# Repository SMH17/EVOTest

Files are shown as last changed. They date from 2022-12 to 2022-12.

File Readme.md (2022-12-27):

Test olive oil quality using a laser diode with wavelength in 405nm-445nm range to check absorbance properties of chlorophyll and elicit its fluorescence and a TCS34725 sensor to analyze color spectrum, considering that chlorophyll fluorescence emission peaks around 680nm-700nm wavelength and chlorophyl absorbance peaks around 400nm-450nm wavelength.
In EVO oils the chlorophyll isn't destroyed by chemical processing and heat treatments, so it gives a clue of oil quality.
It is also important to note that this test cannot directly measure the oil acidity, however if the oil has high acidity level the chlorophyll will degrade faster over the time. 

NOTES:
- The project model and firmware code are just preliminary concept versions that could be improved refining the current analysis method and adding additional modules and test routines to evaluate other aspects.
- This code has been optimized for the use with STM32F030F4P6 and has been tested on STM32F030F4 Demo Board, in order to fit in small flash of this board the default Arduino USART serial support must be disabled.
- This code uses customized libraries so they aren’t available in standard repositories. Use the libraries provided e.g., copying them from libs folder to your Arduino\libraries folder (or configuring them properly for whatever IDE you use).
- Use low power <5mW laser diodes (as the one used for pointers), do not use high power lasers.
- Laser modules even at same wavelength and power level may have different lens configuration and collimation, so you need to do some calibration to get consistent results with different laser modules. 
- The stereolithographic files STL in 3D models libraries can be easily printed with common FDM 3D printer and filaments, however make sure to avoid to use transparent materials that could make filter external light in analysis chamber, this is very important. (I have used black PLA to print my prototype.)

Check [PDF documentation](https://github.com/SMH17/EVOTest/blob/main/EVOTest.pdf) for more details.

Version: 0.1a

Website:
www.silviomarano.tk

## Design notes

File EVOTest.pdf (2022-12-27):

EVOTest by Silvio Marano – v0.1a – 2020

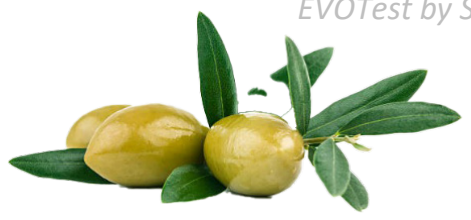
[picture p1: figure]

# EVOTest

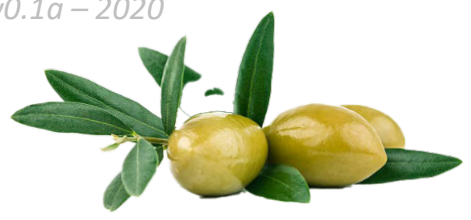
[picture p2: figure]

Olive oil is very appreciated however its quality varies a lot and often is distributed as EVO (extra virgin olive oil) subpar oil that isn’t really eligible for that label.
EVOTest is an open-source electronic project that allows to easily test olive oil quality.

## WORKING PRINCIPLE

An olive oil to be label EVO must be extracted without chemical processing and at temperatures lower than 33°C or lower than 27°C (cold extraction) for the higher quality ones, and an acidity level not higher than 0.8°.
These conditions grant that oil contains chlorophyll that isn't degraded by chemical processing, high temperature heat treatments (all methods used to increase oil extraction quantity at detriment of its characteristics), so its presence gives a clue of oil quality. Chlorophyll has also interesting properties that can be used to evaluate its presence and\or integrity.
EVOTest uses a laser diode with wavelength in 405nm-445nm range to check absorbance properties of chlorophyll and elicit its fluorescence and a sensor to analyze color spectrum, considering that chlorophyll fluorescence emission peaks around 680nm-700nm (red light spectrum) wavelength and chlorophyl absorbance peaks around 400nm-450nm wavelength.

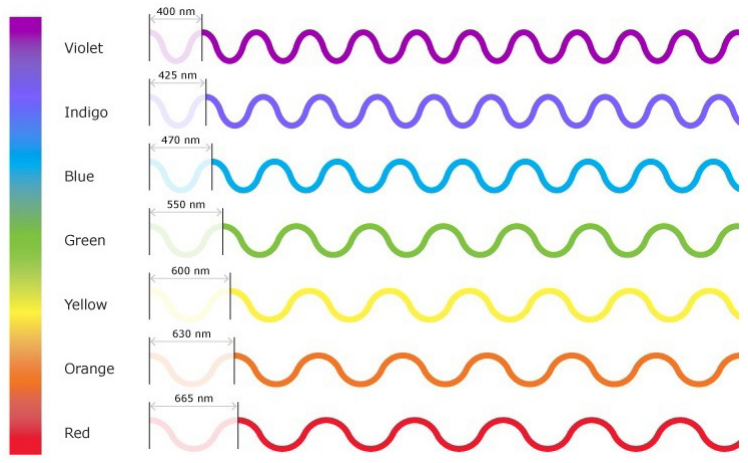
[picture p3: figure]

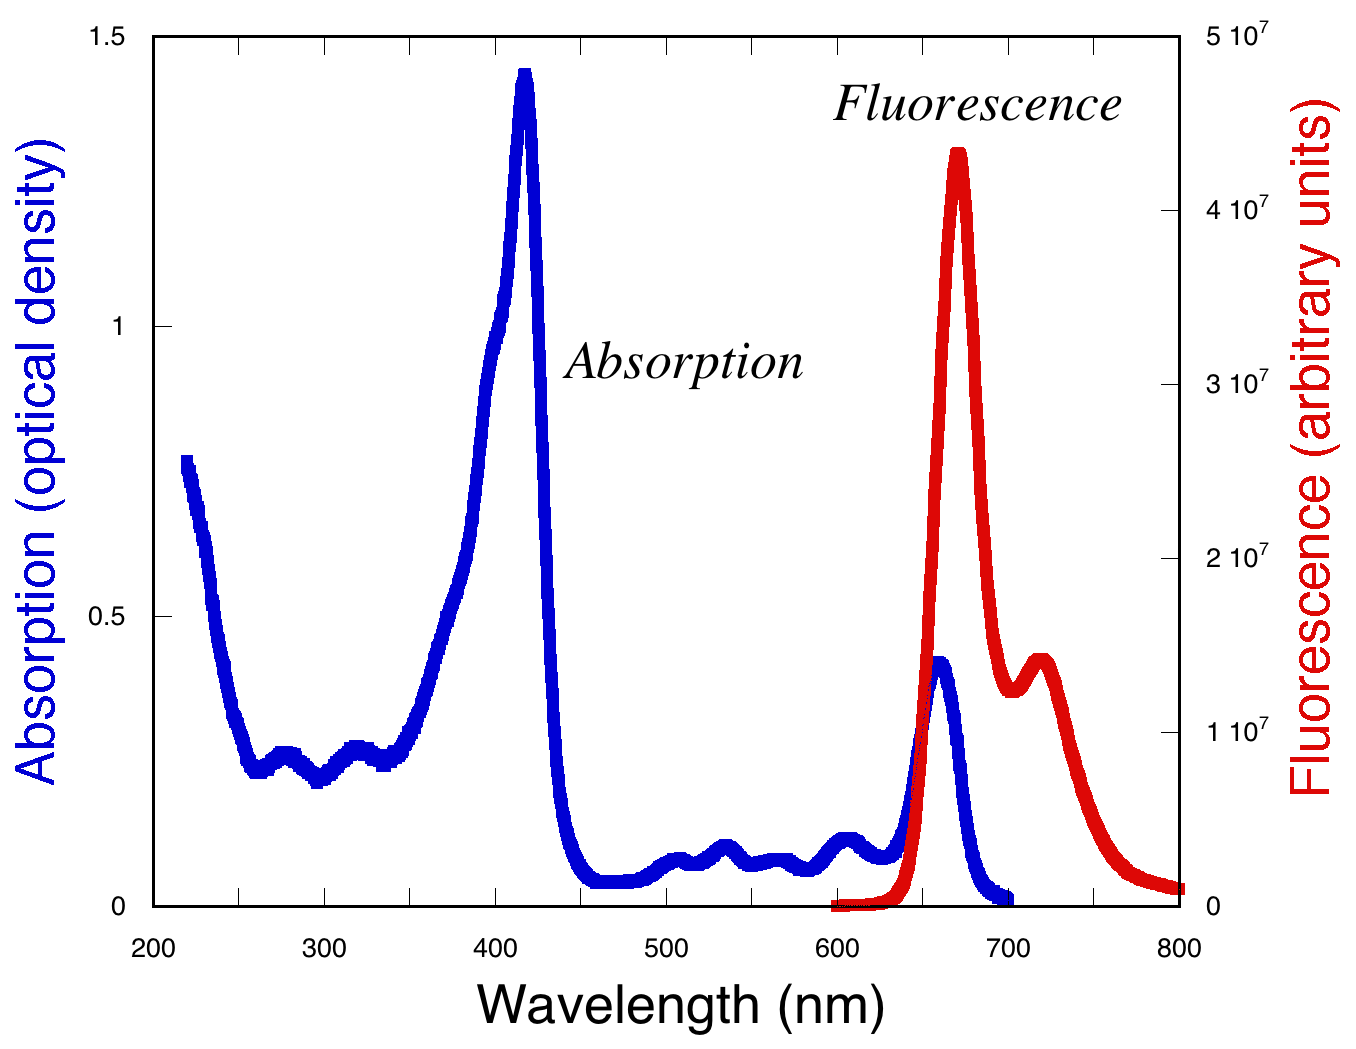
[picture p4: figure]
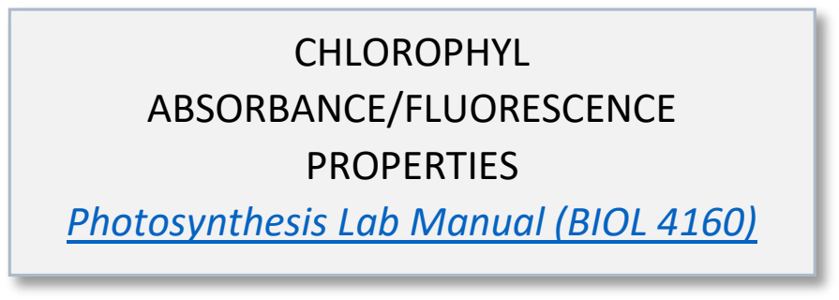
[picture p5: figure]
CHLOROPHYL ABSORBANCE/FLUORESCENCE PROPERTIES Photosynthesis Lab Manual (BIOL 4160)

It is also important to note that this test cannot directly measure the oil acidity, however if the oil has high acidity level the chlorophyll will degrade faster over the time.

The test is also able to determine if the oil tested isn’t olive oil at all, considering that in vegetable oils except olive oil there is a strong fluorescence emission around 430nm-470nm (between indigo and blue light spectrum).

In the table below we can see the sensor RGB channels values of some specimen.

Type | R | G | B
Extra virgin olive oil | 85 | 11 | 20
Bad quality olive oil | 75 | 15 | 70
Seed oil | 30 | 60 | 150

## THE DEVICE

EVOTest consists of a small device powered through microUSB port so that could be powered with common microUSB chargers. COMPONENTS
Here the list of the components used for the prototype
- STM32F030F4 Demo Board, an STM32 MCU with a Cortex-M0 48MHz, 4KB SRAM, 16KB flash storage.
It has been chosen because it is an inexpensive microcontroller unit easily available and it’s enough to meet this project requirements, however nothing prevents you to use something better.

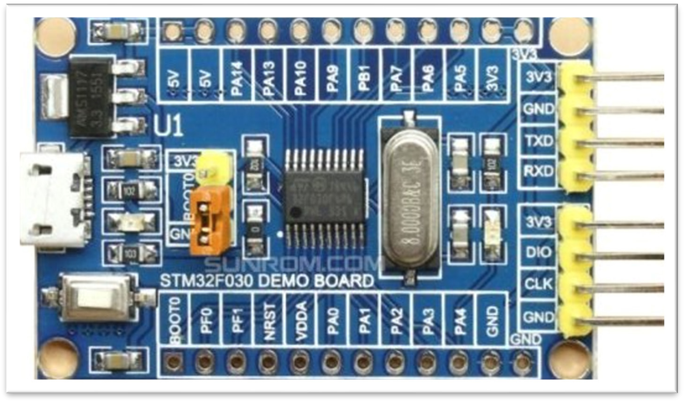
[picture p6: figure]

- 0.91” SSD1306 OLED Display (they are available in 2 versions: white active pixel and blue\yellow active pixels, choosing one version or another doesn’t make any difference).

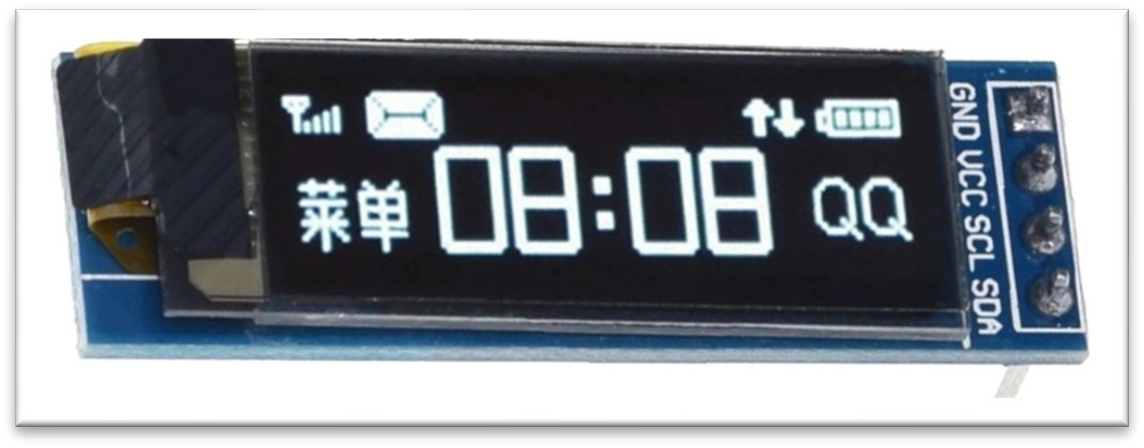
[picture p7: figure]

- TCS34725 color sensor based on a photodiode array, with each photodiode filtered to be sensitive to different light spectrum except one that is unfiltered, in order to output RGBC (red, green, blue, clear) values, the sensing part is located at the center, it has also a LED that can be controlled with LED pin (for our analysis it is switched off).

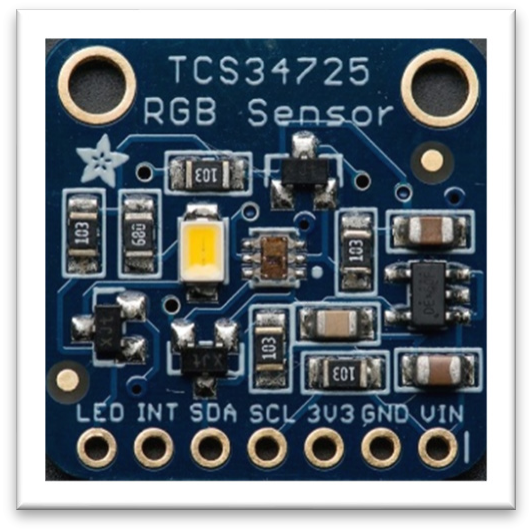
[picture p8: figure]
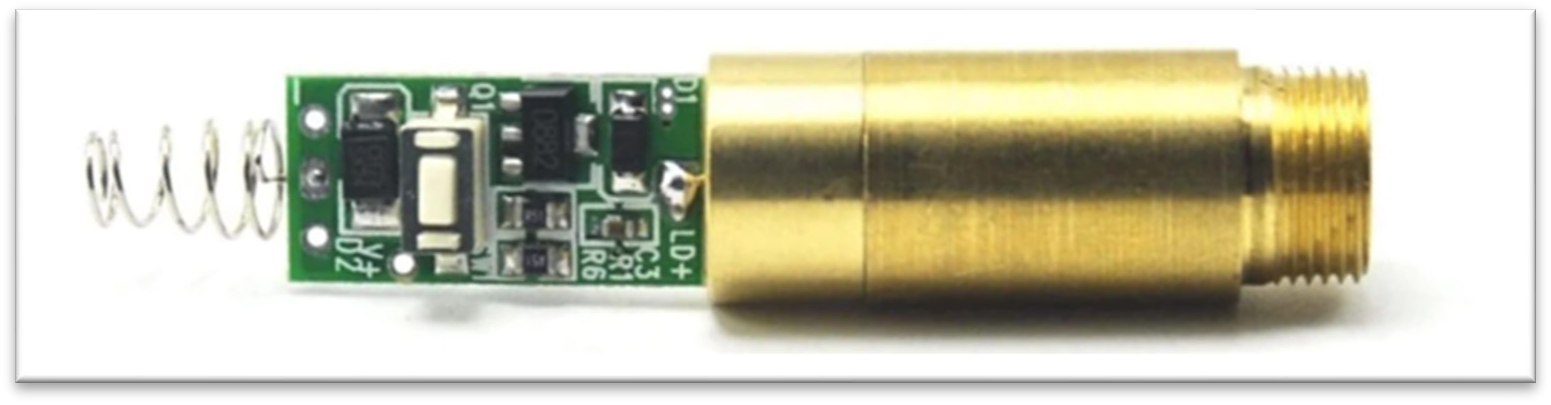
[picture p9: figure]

- 405nm laser module, <5mW power (typically used for purple laser pointer pens).

- F-F DuPont connectors (not needed if as alternative you sold wires and don’t want to have an easy access to SWD programming pins).

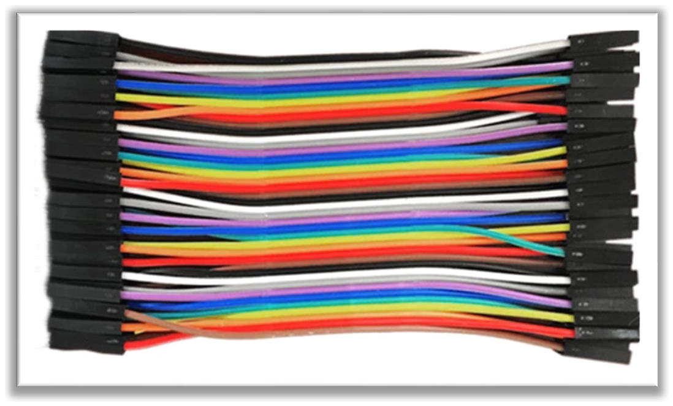
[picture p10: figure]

- Transparent glass pipette 7mm diameter, 50mm length.

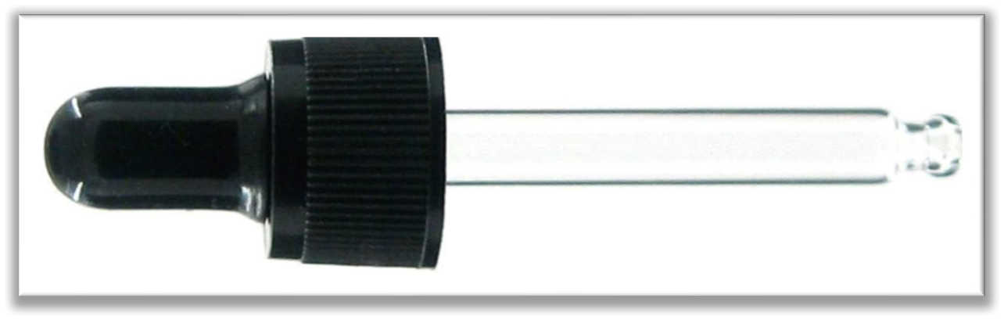
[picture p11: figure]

- Hot glue to keep the parts in place.
- 50g PLA to 3D print all case parts using STL files provided.

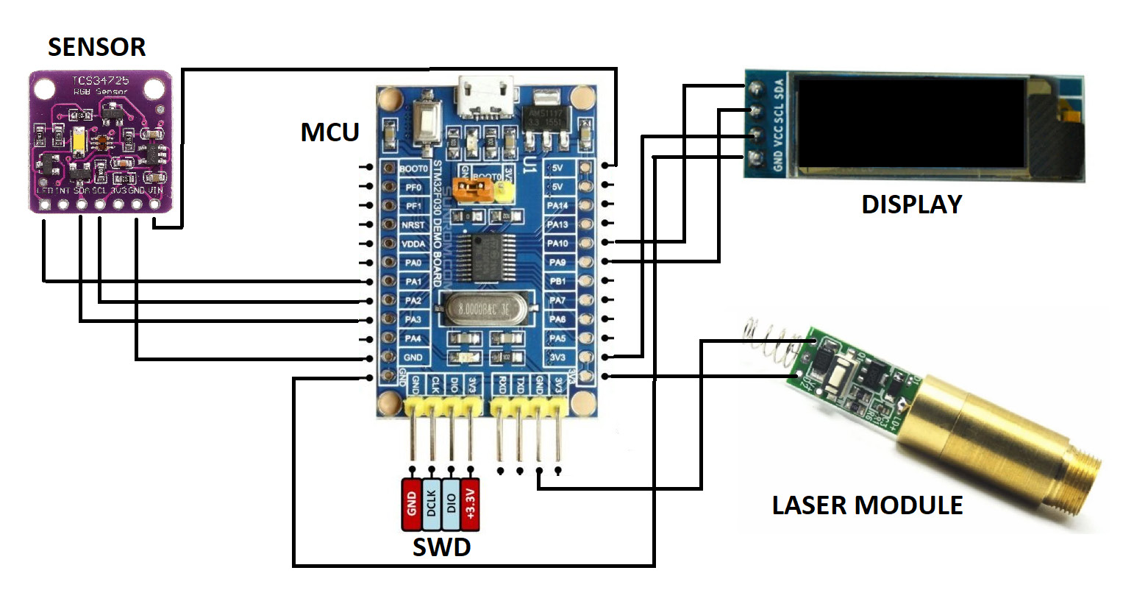
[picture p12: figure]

WIRING

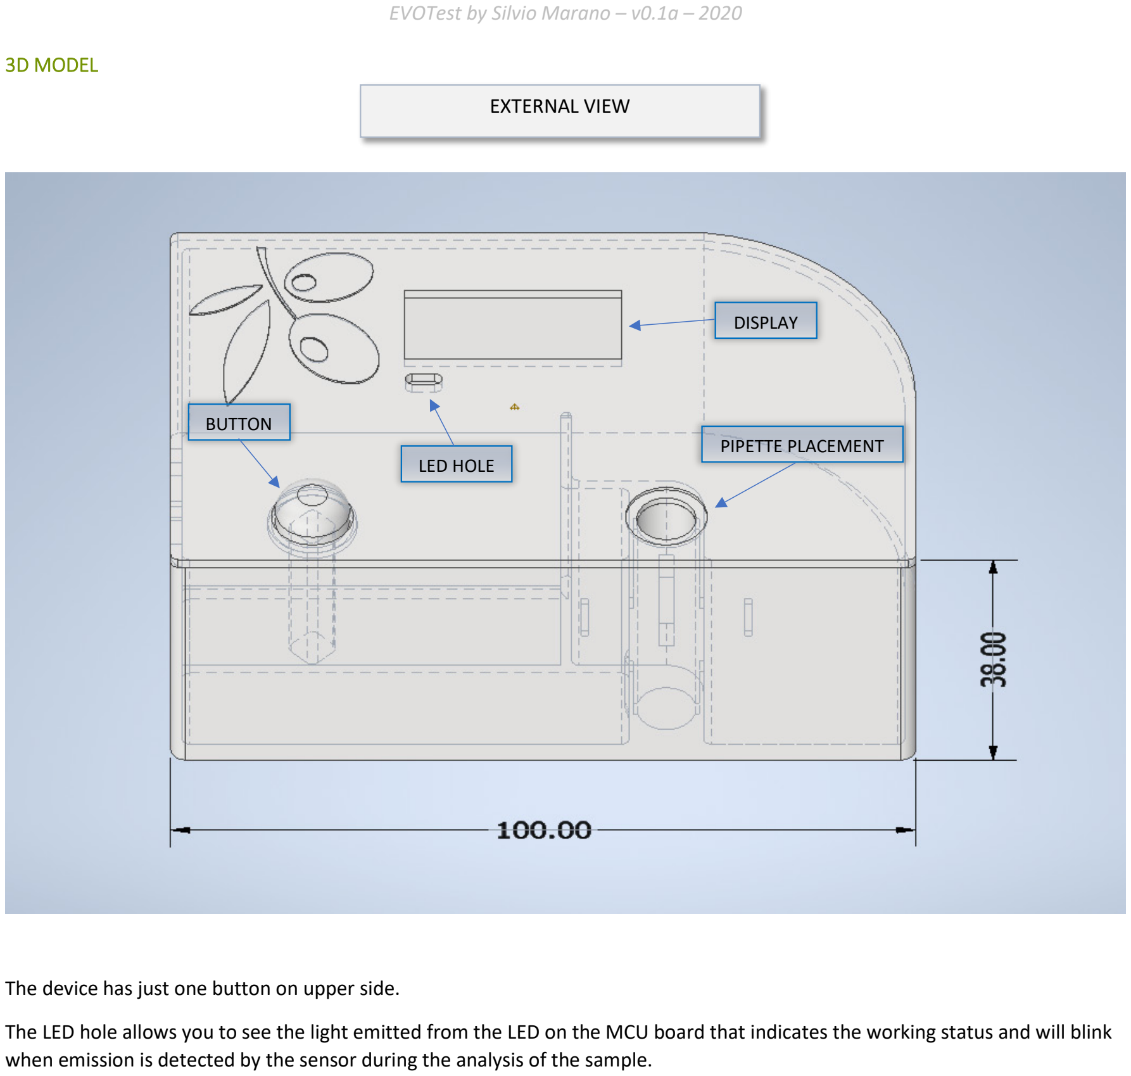
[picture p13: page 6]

3D MODEL

The device has just one button on upper side.
The LED hole allows you to see the light emitted from the LED on the MCU board that indicates the working status and will blink when emission is detected by the sensor during the analysis of the sample.

EXTERNAL VIEW

BUTTON

DISPLAY

PIPETTE PLACEMENT
LED HOLE

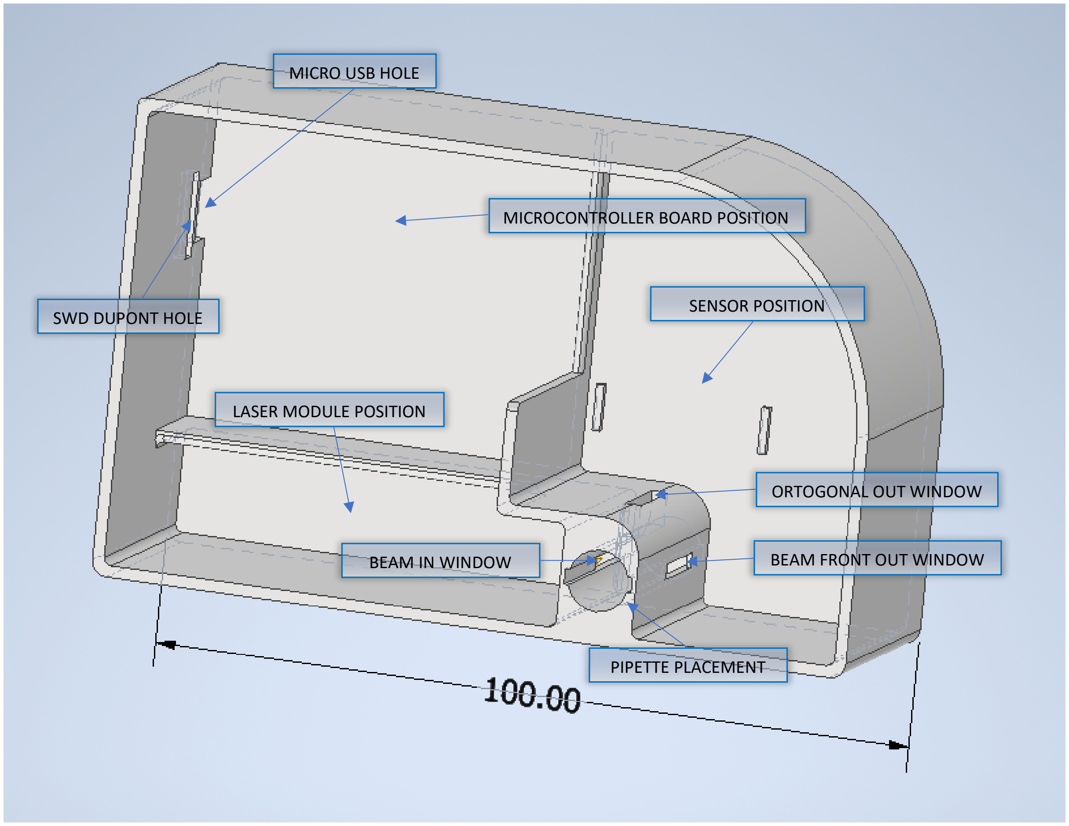
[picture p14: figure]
BEAM FRONT OUT WINDOW; ORTOGONAL OUT WINDOW; SENSOR POSITION; LASER MODULE POSITION; MICROCONTROLLER BOARD POSITION; MICRO USB HOLE; SWD DUPONT HOLE; BEAM IN WINDOW; PIPETTE PLACEMENT

The internal area has 3 sections where you must pay attention to place the various components, making sure that no other light other than the one emitted by the out window of pipette placement could be detected by sensor.
“SWD DuPont hole” is just in order to make the SWD programmer interface accessible from outside without the need to detach the top, in case you want to update the firmware after device assembly; this is realized attaching 4 F-F DuPont jumpers to the board SWD pins and fix them with a bit of hot glue the other end over that hole so that we have an external programmer port. If you are not interested in this feature, you could simply close it.

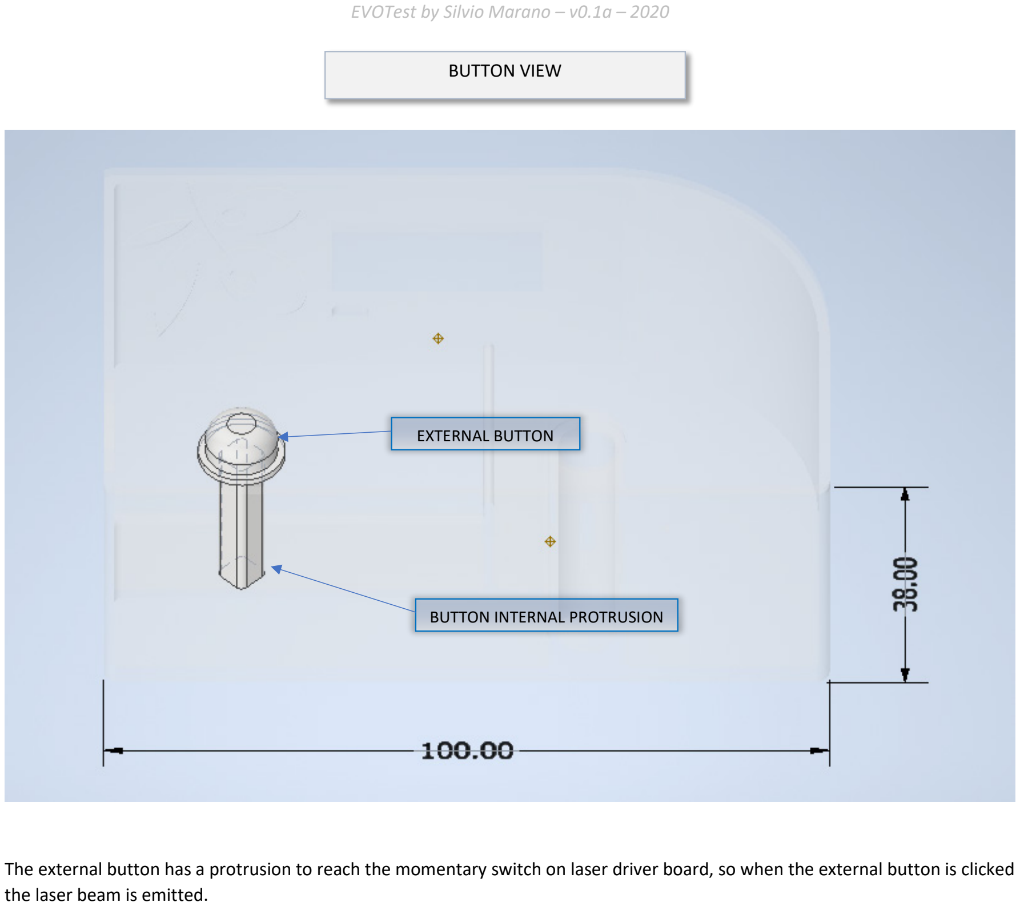
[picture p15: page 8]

The external button has a protrusion to reach the momentary switch on laser driver board, so when the external button is clicked the laser beam is emitted.

BUTTON VIEW

EXTERNAL BUTTON

BUTTON INTERNAL PROTRUSION

## ANALYSIS STEPS

1) Use the pipette to pick an oil sample;
2) Place the pipette with the oil in EVOTest Pipette Placement paying attention to not squeeze it, the oil must remain in the pipette;
3) Click the button to start the analysis, that must be clicked only when the pipette with oil sample is placed in pipette placement.
When the button is pressed the laser pass through the oil in the pipette and fluorescence light emitted by the window orthogonal to the laser beam line hits the sensor. When the sensor is illuminated, the firmware in the microcontroller starts to accumulate various read of the color spectrum, and when the button is released, it calculates the average values for RGB channels, passing the values to the algorithms that calculates the score and finally show the results on the display.

## NOTES

- The project model and firmware code are just preliminary concept versions that could be improved refining the current analysis method and adding additional modules and test routines to evaluate other aspects.
- Direct soldering of the wires without using DuPont jumpers and headers would have allowed a much more compact version of the device to be designed by eliminating the need for sufficient space for the terminals and connector headers, but this would also have made modification more difficult.
- This code has been optimized for the use with STM32F030F4P6 and has been tested on STM32F030F4 Demo Board, in order to fit in small flash of this board (just 16KB) the default USART serial support must be disabled.
- This code uses customized libraries for sensor and display, so they aren’t available in standard repositories. Use the libraries provided e.g., copying them from libs folder to your Arduino\libraries folder (or configuring them properly for whatever IDE you use).
- Use low power <5mW laser diodes (as the one used for pointers), do not use high power lasers.
- Laser modules even at same wavelength and power level may have different lens configuration and collimation, so you may need to do some calibration to get consistent results with different laser modules.
- The stereolithographic files STL in 3D models libraries can be easily printed with common FDM 3D printer and filaments, however make sure to avoid to use transparent materials that could make filter external light in analysis chamber, this is very important. (I have used black PLA to print my prototype.)

## LICENSE TERMS AND CONDITIONS

The project is shared as is. I’m not responsible of any improper use, and I’m not responsible to provide any warranty.
The project is shared for hobbyists, researchers and students under Creative Commons Attribution-NonCommercial-ShareAlike 4.0 International (CC BY-NC-SA 4.0) license.
This license allows users to distribute, remix, adapt, and build upon your work non-commercially, as long as they give appropriate credit, provide a link to the license, and share derivative works and modifications they make under the same terms.
License Link: http://creativecommons.org/licenses/by-nc-sa/4.0/

For any other use that doesn't fit the above category, contact me using the module on my website http://silviomarano.tk

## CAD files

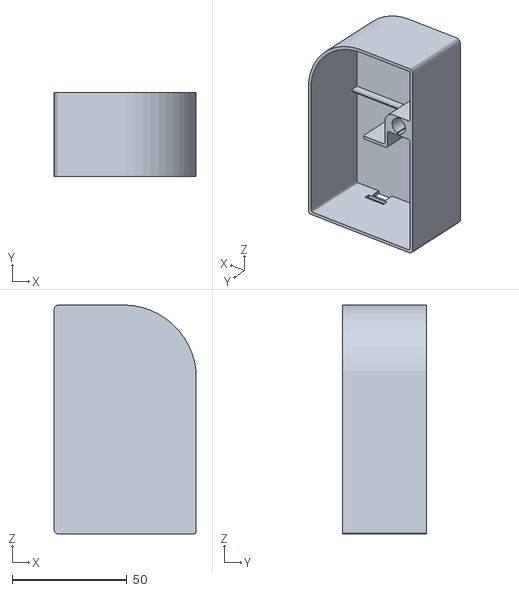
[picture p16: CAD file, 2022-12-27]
3D Model/EvoTest_body.stl
62.0 x 36.5 x 100.0

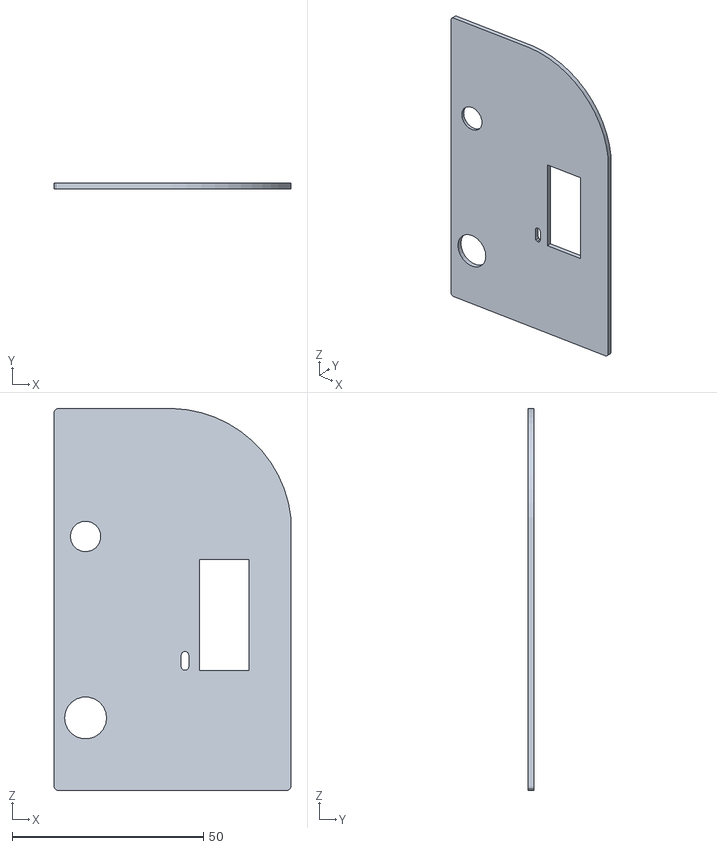
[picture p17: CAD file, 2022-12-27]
3D Model/EvoTest_top.stl
62.0 x 1.50 x 100.0

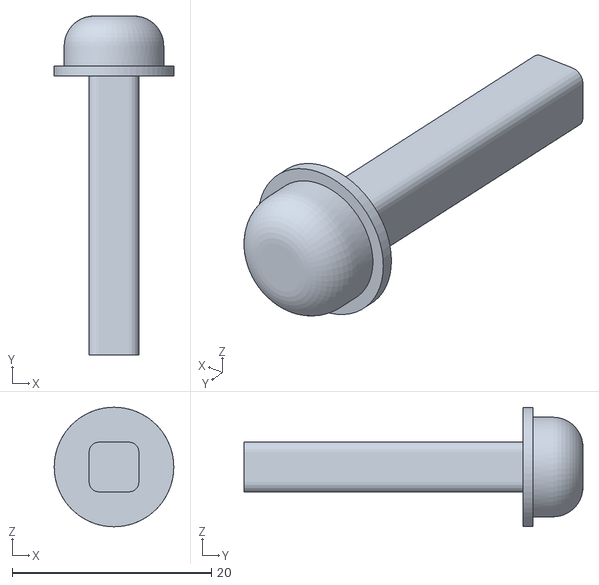
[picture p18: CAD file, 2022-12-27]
3D Model/EvoTest_button.stl
12.0 x 34.0 x 12.0

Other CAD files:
3D Model/EVOTest.iam
3D Model/EvoTest_body_bottom_closed.ipt
3D Model/EvoTest_button.ipt
3D Model/EvoTest_top.ipt

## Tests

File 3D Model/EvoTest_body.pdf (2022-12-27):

setPageBoxes("Crop", 0, 0, [0,2000,2000,0]);

TITOLO | EVOTest N. PARTE | EvoTest_body REVISIONE PROGETTISTA | Silvio Marano INGEGNERE | Silvio Marano NOTE

LE INFORMAZIONI E/O IL MATERIALE CONTENUTI IN QUESTO DOCUMENTO SONO DI PROPRIETÀ DELLʼAUTORE E COSTITUISCONO INFORMAZIONI E/O MATERIALE RISERVATI DELLʼAUTORE. TALI INFORMAZIONI NON POSSONO ESSERE UTILIZZATE, RIPRODOTTE, PUBBLICATE O DIVULGATE A TERZI SE NON IN POSSESSO DI AUTORIZZAZIONE SCRITTA.

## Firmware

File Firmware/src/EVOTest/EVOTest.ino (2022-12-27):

/*
-------------------------
EVOTest by Silvio Marano
-------------------------
Test olive oil quality using a <5mW laser diode with wavelength in 405nm-445nm range to check absorbance properties of chlorophyll and elicit its fluorescence and a TCS34725 color sensor to analyze color spectrum, considering that chlorophyll fluorescence emission peaks around 680nm-700nm wavelength and chlorophyl absorbance peaks around 400nm-450nm wavelength.
In EVO oils the chlorophyll isn't destroyed by chemical processing and heat treatments, so it gives a clue of oil quality.
It is also important to note that this test cannot directly measure the oil acidity, however if the oil has high acidity level the chlorophyll will degrade faster over the time. 


NOTES:
- The project model and firmware code are just preliminary concept versions that could be improved refining the current analysis method and adding additional modules and test routines to evaluate other aspects.
- This code uses customized libraries so they aren’t available in standard repositories. Use the libraries provided e.g., copying them from libs folder to your Arduino\libraries folder (or configuring them properly for whatever IDE you use).
- This code has been optimized for the use with STM32F030F4P6 and has been tested on STM32F030F4 Demo Board, in order to fit in small flash of this board the default Arduino USART serial support must be disabled.
- Check documentation for more details.


Version: 0.1a

Website:
www.silviomarano.tk

*/
#include <miniOled.h>
#include <Micro_TCS34725.h>

Micro_TCS34725 tcs = Micro_TCS34725(TCS34725_ADDRESS, TCS34725_INTEGRATIONTIME_50MS, TCS34725_GAIN_60X);

bool calibrationMode = false;             // manually set to true for testing
bool sensorWorks = false;                 // sensor initialization finished without errors
bool detecting = false;                   // true if sensor is detecting light
bool detected = false;                    // detection cycle is completed
int waitCounter = 0;                      // to count the number of cycles without anything sensed
int sampleCounter = 0;                    // to count the samples used to calculate the average values for the sample
bool displayOff = false;                  // display standby status
int score = -1;                           // olive oil quality score, -1 means it isn't not olive oil
uint16_t red, green, blue, clear;         // sensor RGBC channels output
int redRes, greenRes, blueRes, clearRes;  // average RGBC channels values used for result calc
const int maxSamples = 100;               // the max number of reads used for estimate the average RGB values of the sample
uint16_t oilSample[4][maxSamples];        // the oil sample matrix with the RGB reads of the sensor


void setup() {

  // initialize digital pin LED_BUILTIN as an output.
  pinMode(LED_BUILTIN, OUTPUT);

  if (tcs.begin()) {
    //Serial.println("Found sensor");
    sensorWorks = true;
  }
  // initialize digital pin PA1 attached to TCS34725 color sensor LED pin as an output.
  pinMode(D1, OUTPUT);
  // turn off TCS34725 color sensor LED
  digitalWrite(D1, LOW);

  Oled.init();  //initialze OLED display
  Oled.wideFont = false;
  Oled.smallFont = true;
  Oled.chrSpace = 1;

  if (sensorWorks) {
    Oled.printString("EVOTest by S. Marano ", 0, 0);
    Oled.drawLine(1, 0xa0);
    //Oled.printString("Carica un campione e  clicca il pulsante.", 0, 2);
    Oled.printString("Load a sample, and  click the button.", 0, 2);
  } else {
    Oled.printString("Sensor Error", 0, 0);
  }
}

void loop() {
  tcs.getRGBC(&red, &green, &blue, &clear);
  // if all color channels are at 0 it means that color sensor is detecting nothing so there isn't any light in the detection chambers of the device, so we are in a waiting status
  if (red > 0 | green > 0 | blue > 0) {
    // if the display is in standby it must be powered on again
    if (displayOff) {
      Oled.setPowerOn();
    }
    detecting = true;
    if (!detected) {
      Oled.clearDisplay();
      //Oled.printString("Analisi...", 2, 2);
      Oled.printString("Analyzing...", 2, 2);
    }
    // till the button is pressed and the counter hasn't reached max, the oil sample matrix is populated with a new read each cycle
    if (sampleCounter < maxSamples) {
      oilSample[sampleCounter][0] = red;
      oilSample[sampleCounter][1] = green;
      oilSample[sampleCounter][2] = blue;
      oilSample[sampleCounter][3] = clear;
      sampleCounter++;
    } else {
      // if we have reached max number of samples the matrix can hold, the second half of the matrix is overwritten
      sampleCounter = maxSamples / 2;
    }

    // blinking on board LED to indicate the activity
    digitalWrite(LED_BUILTIN, HIGH);
    delay(50);
    digitalWrite(LED_BUILTIN, LOW);
    delay(50);

    detected = true;
    waitCounter = 0;
  } else {
    detecting = false;
    // it isn't healthy to have the display always on, so if it isn't detected any activity for long, the display is switched off
    if (waitCounter > 5000) {
      if (!displayOff) {
        Oled.clearDisplay();
        Oled.setPowerOff();
        displayOff = true;
      }
    } else {
      waitCounter++;
    }
  }
  if (detected && !detecting) {
    Oled.clearDisplay();
    //Oled.printString("Valutazione...", 2, 2);
    Oled.printString("Evaluating...", 2, 2);

    // now we calculate the average value and then use this value to determine the score
    int redsum = 0, greensum = 0, bluensum = 0, clearSum = 0;
    for (int i = 0; i < sampleCounter; ++i) {
      redsum += oilSample[i][0];
      greensum += oilSample[i][1];
      bluensum += oilSample[i][2];
      clearSum += oilSample[i][3];
    }
    redRes = redsum / sampleCounter;
    greenRes = greensum / sampleCounter;
    blueRes = bluensum / sampleCounter;
    clearRes = clearSum / sampleCounter;
    sampleCounter = 0;
    score = evoTest(redRes, greenRes, blueRes);

    Oled.clearDisplay();
    if (calibrationMode) {
      sampleDetails();
    } else {
      if (score > 95) {
        //Oled.printString("Ottimo olio d'oliva  extravergine!", 0, 0);
        Oled.printString("Excellent extra virgin olive oil!", 0, 0);
      } else if (score > 65) {
        //Oled.printString("Buon olio d'oliva  extravergine!", 0, 0);
        Oled.printString("Good extra virgin  olive oil!", 0, 0);
      } else if (score > 58) {
        //Oled.printString("Olio d'oliva di  media qualita'!", 0, 0);
        Oled.printString("Medium quality olive oil!", 0, 0);
      } else if (score > 45) {
        //Oled.printString("Olio d'oliva di  bassa qualita'!", 0, 0);
        Oled.printString("Low quality olive oil!", 0, 0);
      } else if (score > -1) {
        //Oled.printString("Olio d'oliva di  pessima qualita'!", 0, 0);
        Oled.printString("Bad quality olive oil!", 0, 0);
      } else {
        //Oled.printString("Non e' olio d'oliva!", 0, 0);
        Oled.printString("It's definitely not  olive oil!", 0, 0);
      }
      Oled.drawLine(2, 0xe0);
      //Oled.printString("PUNTEGGIO: ", 3, 3);
      Oled.printString("SCORE: ", 3, 3);
      Oled.printInt(score, 4, 4);
    }
    detected = false;
  }
}

void sampleDetails() {
  Oled.printString(" R: ", 0, 0);
  Oled.printInt(redRes, 4, 0);
  Oled.printString(" G: ", 0, 1);
  Oled.printInt(greenRes, 4, 1);
  Oled.printString(" B: ", 0, 2);
  Oled.printInt(blueRes, 4, 2);
  Oled.printString(" C: ", 0, 3);
  Oled.printInt(clearRes, 4, 3);
  Oled.printString(" Score: ", 0, 4);
  Oled.printInt(score, 4, 4);
}

// assign a score to the oil sample according the color spectrum detected in reaction to violet laser
int evoTest(uint16_t redSensor, uint16_t greenSensor, uint16_t blueSensor) {
  int result = 0;
  int greenBlue = greenSensor + blueSensor;
  int redMargin = redSensor - greenBlue;
  if (redMargin > 0) {
    // good absorbance and red fluorescence, likely extravirgin olive oil
    if (redSensor > 2 * greenBlue) {
      // very good absorbance and significant red fluorescence, likely a good quality extravirgin olive oil
      result += 20;
      if (greenBlue < 20) {
        // excellent absorbance and significant red fluorescence, likely a top quality extravirgin olive oil
        result += 20;
      }
    }
    result += 58 + (redMargin / 20);
  } else if (greenBlue <= 2 * redSensor) {
    // absorbance low for an evo and red fluorescence weak, likely a cheap olive oil
    result += 48 + (redMargin / 20);
  } else {
    // absorbance too low and red fluorescence insignificant if any, it's not olive oil
    result = -1;
  }
  return result;
}
